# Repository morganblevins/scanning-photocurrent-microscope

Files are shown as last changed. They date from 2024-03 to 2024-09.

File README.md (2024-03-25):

# scanning-photocurrent-microscope

| Todos | Description + Statues |
| --- | --- |
| `Integrate visible laser into SPCM; get first reflection image` | **Done:** Results below |
| `Get visible light photocurrent scan from PbTaSe2` | **In progress** |
| `Integrate QCL into SPCM` | **Not started** Need to order periscope equiptment |

This repository contains the following for the scanning photocurrent microscope in MIT META lab:
* MATLAB code for controlling and collecting measurments
* Comprehensive part list and photo documentation of build
* Preliminary data

Example of a scanning reflection map of a 30 micron gold cross mark compared to a microscope image

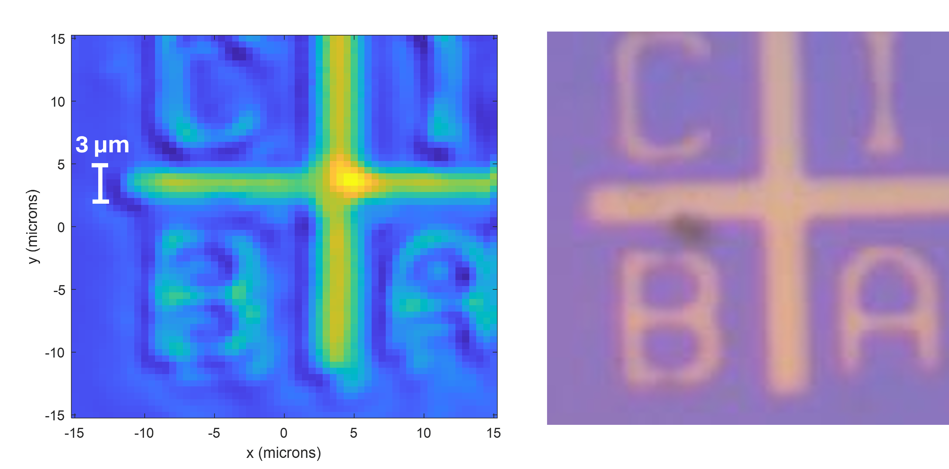
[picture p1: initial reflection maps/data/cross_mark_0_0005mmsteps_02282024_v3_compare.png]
Reflection map of 30 micron cross mark.


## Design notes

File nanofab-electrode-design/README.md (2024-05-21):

To use:
1. Run MatLab code and generate the input file to python code
2. Run Python code and generate the KLayout file.

On running MatLab code:
1. Change the electrodes length and width definitions for the electrodes, if needed. More notes below
2. Follow the prompts as they show up. Remember the order of corners when you click them (starts with 1) as you will be prompted to enter the two that will serve as the main electrode axis.

On running Python code:
1. Open KLayout Macro development, under "python", create a new "general macro (.lym)" file, paste the entire python code into the file;
2. Modify the input and output paths and file names given at the top of the code;
3. Modify route width, drawing layer, and the end electrodes width if needed;
4. Save and run the file in KLayout.

On opening the file in KLayout:
1. Open the silicon die template file in KLayout
2. While template file opened, go to "file -> open" again and open the file just generated by the code
3. Choose "add to current panel" when prompted

Things to note in MatLab code:
1. Electrodes width and length definitions are messed up. The value you enter will undergo transformations along with other shape objects and become some different value. May require some trial-and-error to find the right value.
2. Image does not display the order in which you clicked the corners, which can be hard to use since you have to remember it.

Things to note in Python code:
1. Routing modes are limited. Function docstrings in the code points to where they may be modified and improved
2. See details in routing main code docstring. Routing makes assumptions about which coordinates corresponds to nanostructure and electrodes, but these assumptions can actually be removed by interpreting the input file (from MatLab) differently, since the file indicates which coordinates are nanostructure and which are electrodes (right now these text indications are being ignored)



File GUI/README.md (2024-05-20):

GUI for the SPCM coded in MATLAB by Brady Cruse during Spring 2024 UROP

The GUI is broke up into 5 files

-BBD302_control_keithely2400

-Connection.m

-disconnected.m

-Home.m

The main app is coded in 'GUI.mlapp'.

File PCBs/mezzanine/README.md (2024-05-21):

Mezzanine PCB designed by Jacqueline Wang during Spring 2024 UROP using KiCAD

https://gitlab.com/kicad/libraries/kicad-footprint-generator

the silicondie.py file was ran inside the library-> KiCADModTree->examples folder
### Rendering


### Pad numbering


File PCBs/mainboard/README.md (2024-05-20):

Mainboad PCB files created by Brady Cruse during Spring 2024 UROP using Altium and EasyEDA

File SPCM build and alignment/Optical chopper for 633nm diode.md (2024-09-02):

**August 29th, 2024**

Note, <span style="color: black;">I followed the alignment procedure in the “alignment procedure” document. <span style="color: black;">Very important to have alignment of the beamsplitter, compensator, and the objective and PMT.</span></span>

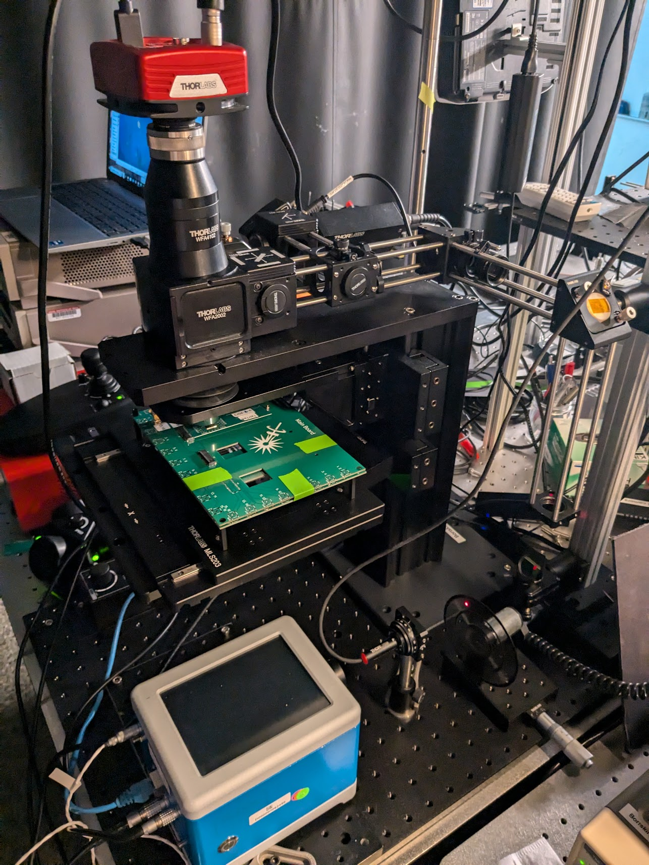
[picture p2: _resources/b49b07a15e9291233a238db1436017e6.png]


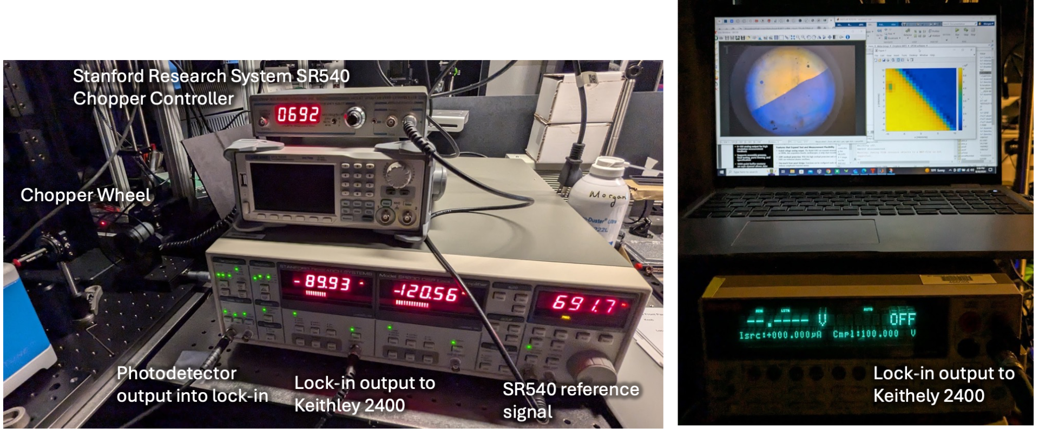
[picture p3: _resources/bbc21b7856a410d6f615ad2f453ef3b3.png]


**Procedure:**

1.  1<span style="color: black;">Position the chopper wheel in front of the laser such that the laser hits the outer slots</span>
2.  <span style="color: black;">Connect the SR540 ‘f’ output to the the reference input of the SR830 Lock-in amp</span>
3.  <span style="color: black;">Turn on the SR540 and set to desired frequency (avoid 60 Hz and its harmonics)</span>
4.  <span style="color: black;">The SR830 lock in should immediately pick up the reference frequency and track is very easily</span>
5.  <span style="color: black;">Connect the photodetector output to the SR830 input A and select current measurement</span>
6.  <span style="color: black;">Set SR830 Channel 1 to display X or R (I did X in this test)</span>
7.  <span style="color: black;">Set SR830 Channel 2 to display phase (theta)</span>
8.  <span style="color: black;">Adjust setting of SR830 until Channel 2 phase is constant (follow 2f rule,</span> <span style="color: black;">etc</span><span style="color: black;">)</span>
9.  <span style="color: black;">Connect the Channel 1 output to the Keithley 2400 and perform a scanning map over a gold-silicon interface on a wafer</span>

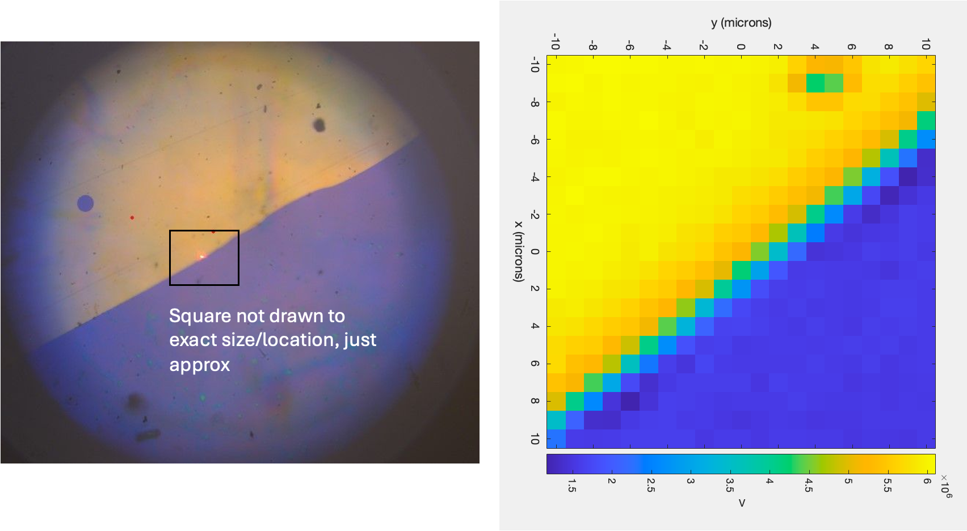
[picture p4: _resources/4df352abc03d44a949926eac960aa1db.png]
<span style="color: black;"></span>

<span style="color: black;"><span style="color: black;">This is the best reflection map I’ve ever gotten!! The gradation is</span> <span style="color: black;">really nice</span> <span style="color: black;">and exact. And it seems to even pick up a little hole in the upper right side.</span></span>

Note,

- <span style="color: black;">The PMT gets saturated depending on the gain you use to power it, so it may show “overload” if the conditions are too bright in the room. Reduce gain or lower lighting</span>
- There is an extra 635 bandpass filter in Mathias’ cupboard- may add this in front of the PMT to get rid of this issue.
- In this test I used a 30ND filter and had 1 small over-the-optical-bench light on

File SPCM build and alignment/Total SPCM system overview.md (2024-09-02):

# Overview of systems

The SPCM takes simultaneous photocurrent and reflection maps 

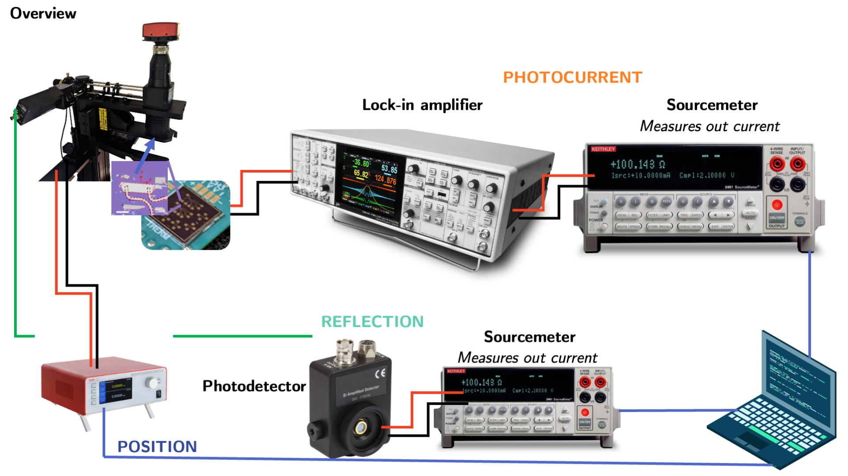
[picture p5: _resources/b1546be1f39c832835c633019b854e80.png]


# Optics

## <span style="color: black;">Optical path from lasers to samples</span>

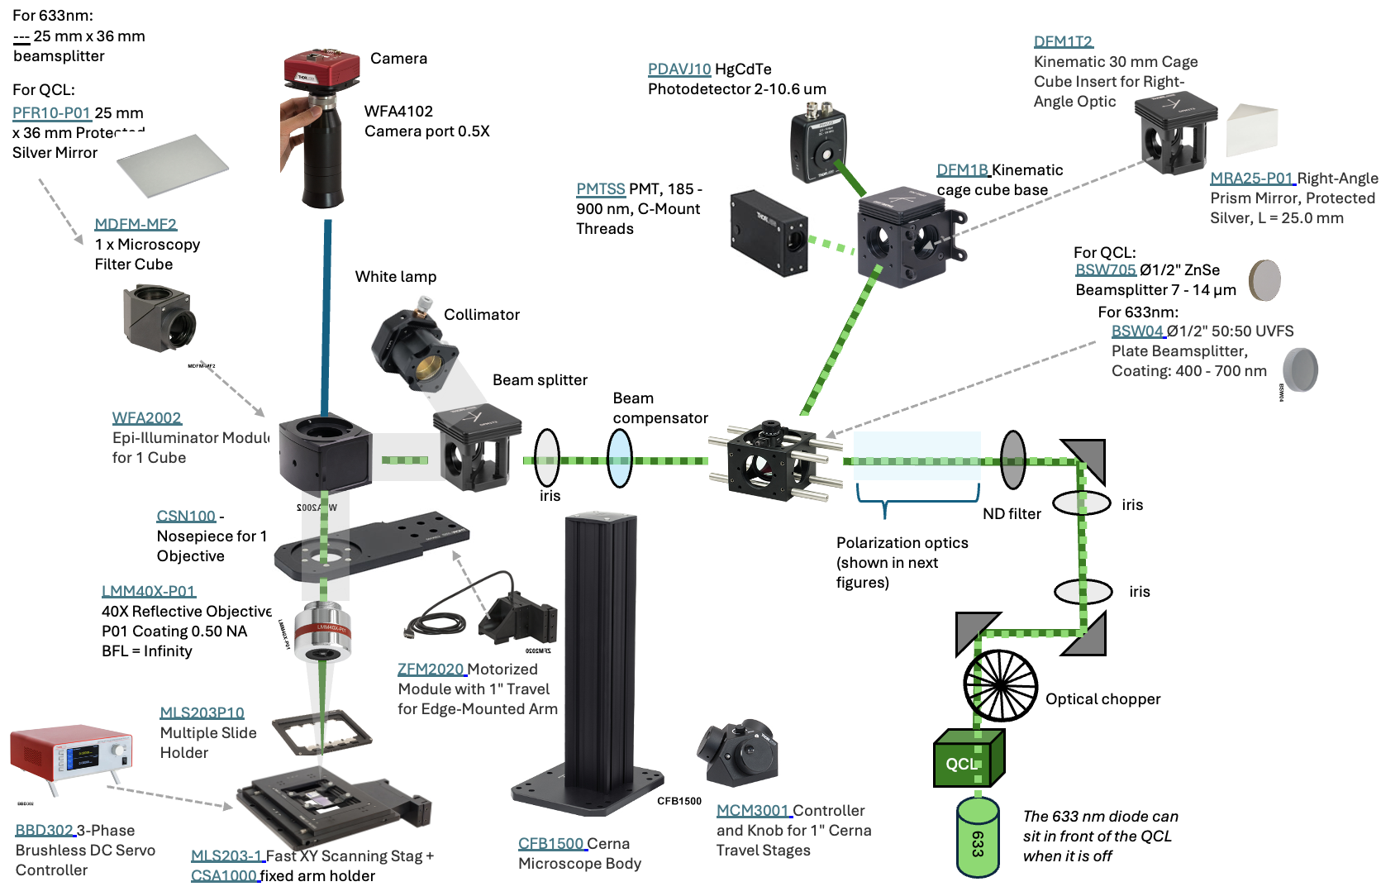
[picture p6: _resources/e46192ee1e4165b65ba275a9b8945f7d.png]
<span style="color: black;"></span>

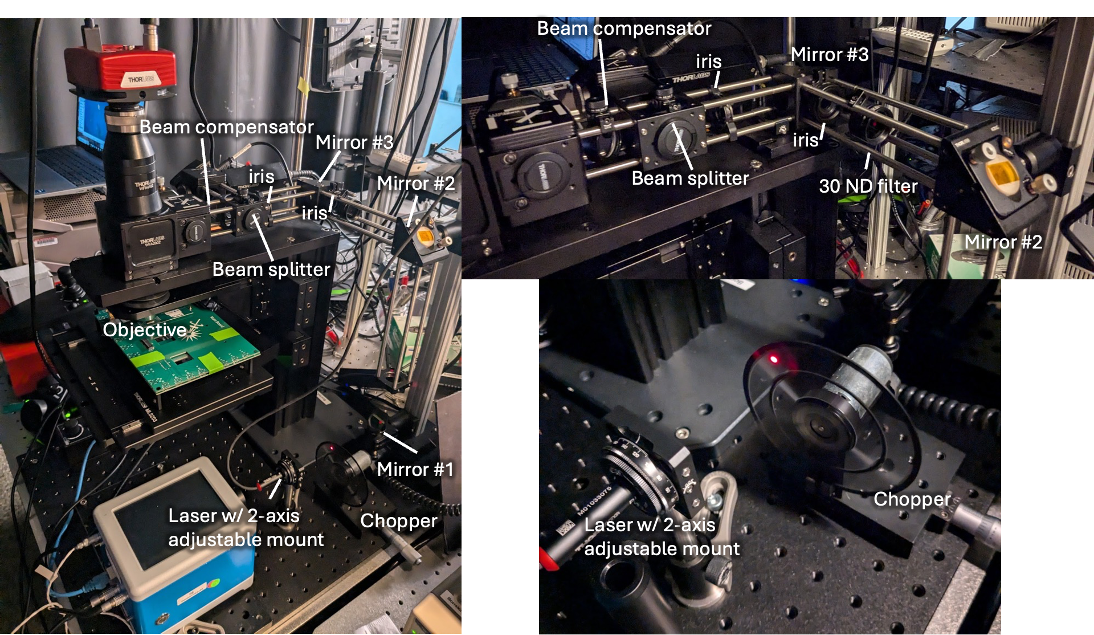
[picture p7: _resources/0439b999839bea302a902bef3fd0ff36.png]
<span style="color: black;"></span>

## <span style="color: black;"><span style="color: black;">Polarization optics for 633 nm laser diode</span></span>

### <span style="color: black;">C</span><span style="color: black;">reating linearly polarized 633 nm laser diode</span>

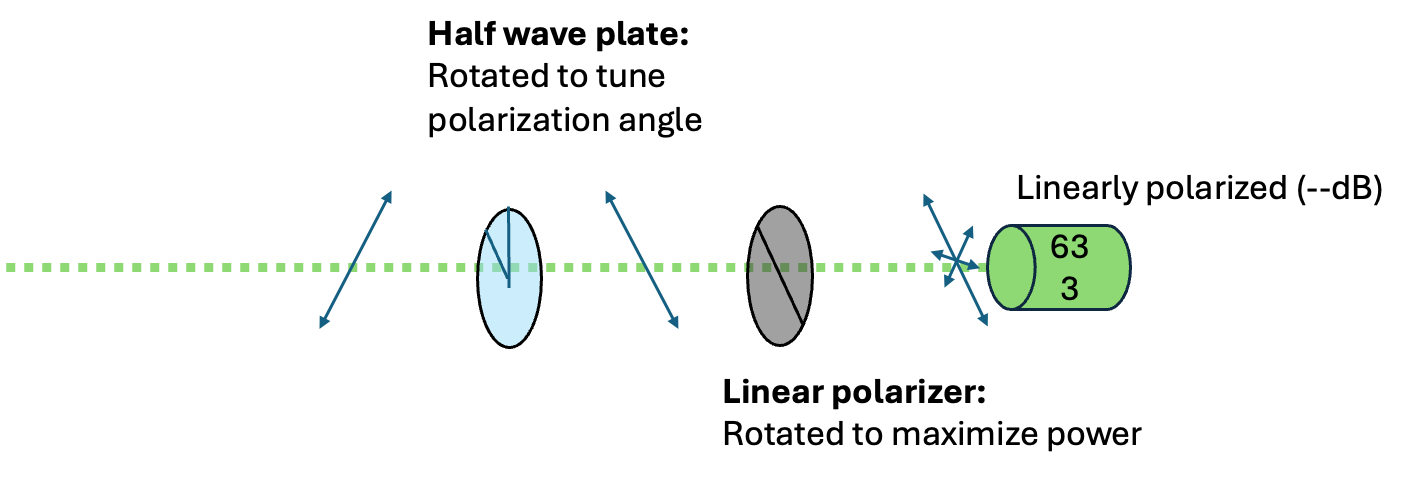
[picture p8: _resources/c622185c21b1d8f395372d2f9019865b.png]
<span style="color: black;"></span>

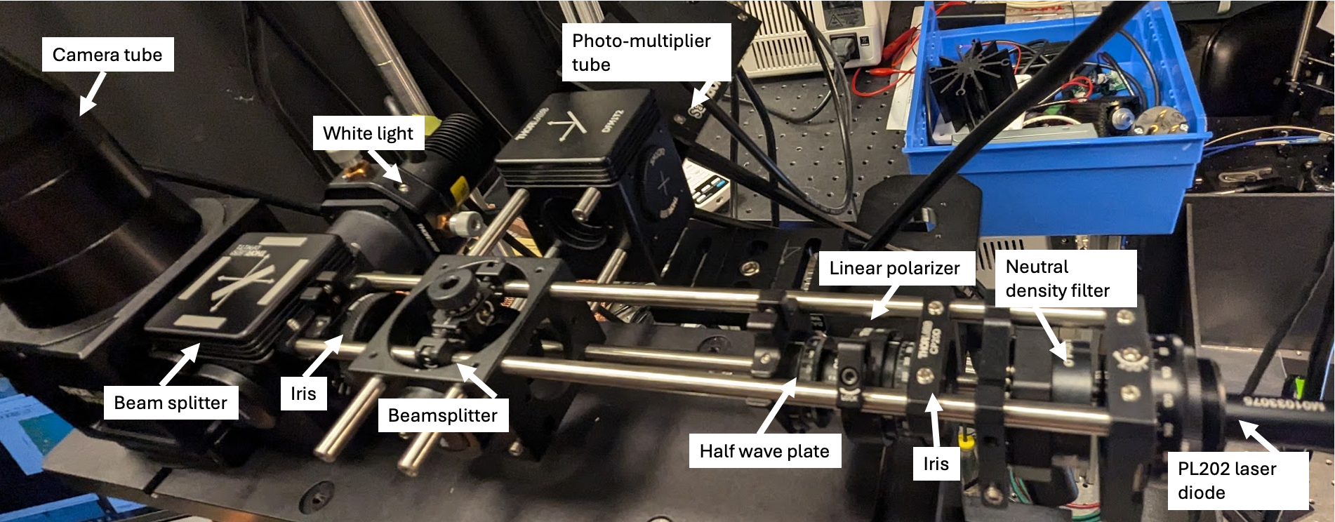
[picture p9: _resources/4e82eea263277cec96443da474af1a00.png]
<span style="color: black;"></span>

### <span style="color: black;"><span style="color: black;">C</span><span style="color: black;">reating circularly polarized 633 nm laser diode</span></span>

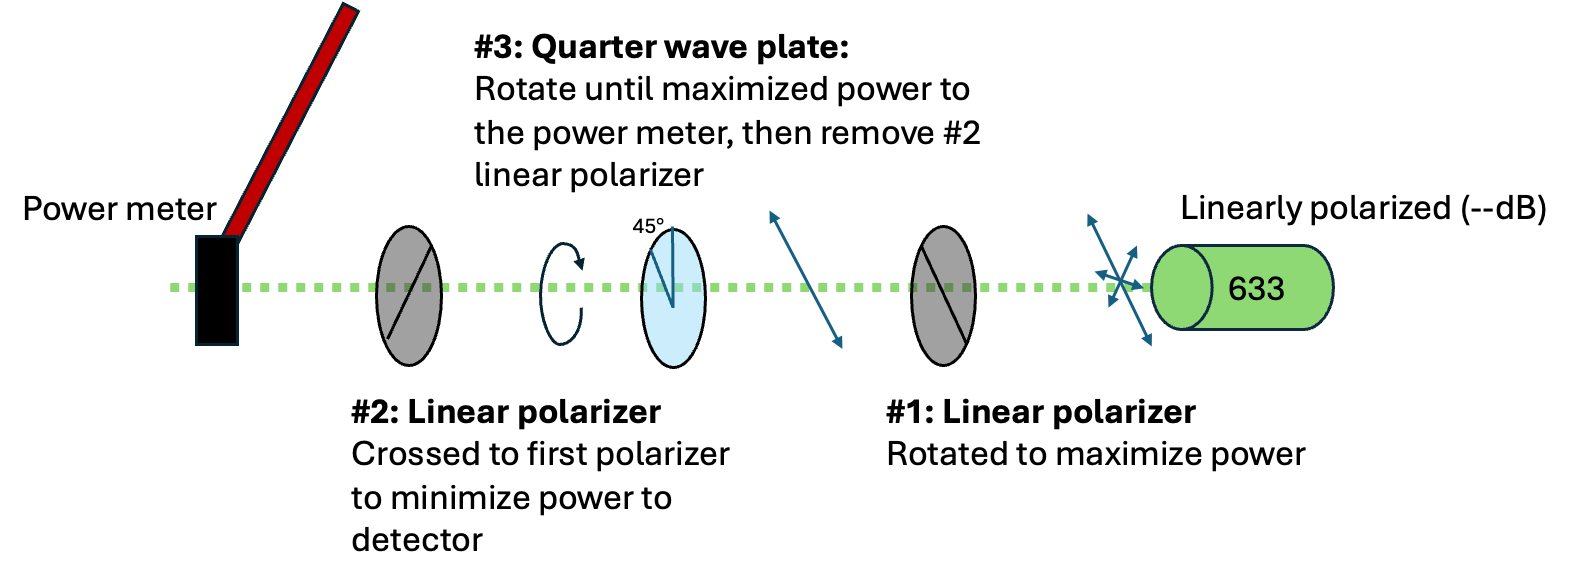
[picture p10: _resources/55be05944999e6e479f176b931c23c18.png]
<span style="color: black;"><span style="color: black;"></span></span>

<span style="color: black;"><span style="color: black;"><span style="color: black;">Two linear polarizers are used before and after the QWP along with a power meter. I kept the first LP static, so it still maximizes the power out of the PL202 laser. Then, without the QWP in the system, I crossed the two polarizers so that no power reached the power meter. Then I added the QWP between them and rotated it until I maximized power to the power meter. This occurs when the fast axis of the QWP is 45 degrees rotated from the input linearly polarized light. Thus, when I remove the second LP, I have circularly polarized light (illustrated in the Edmund optics diagram below).</span></span></span>

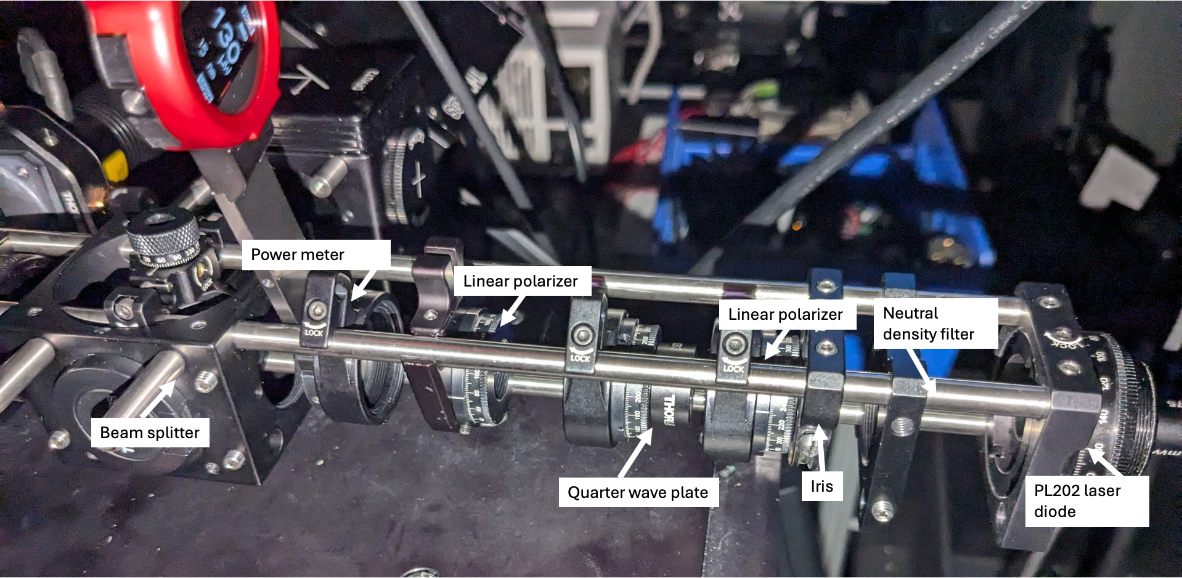
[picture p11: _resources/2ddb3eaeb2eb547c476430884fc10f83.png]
<span style="color: black;"><span style="color: black;"><span style="color: black;"></span></span></span>

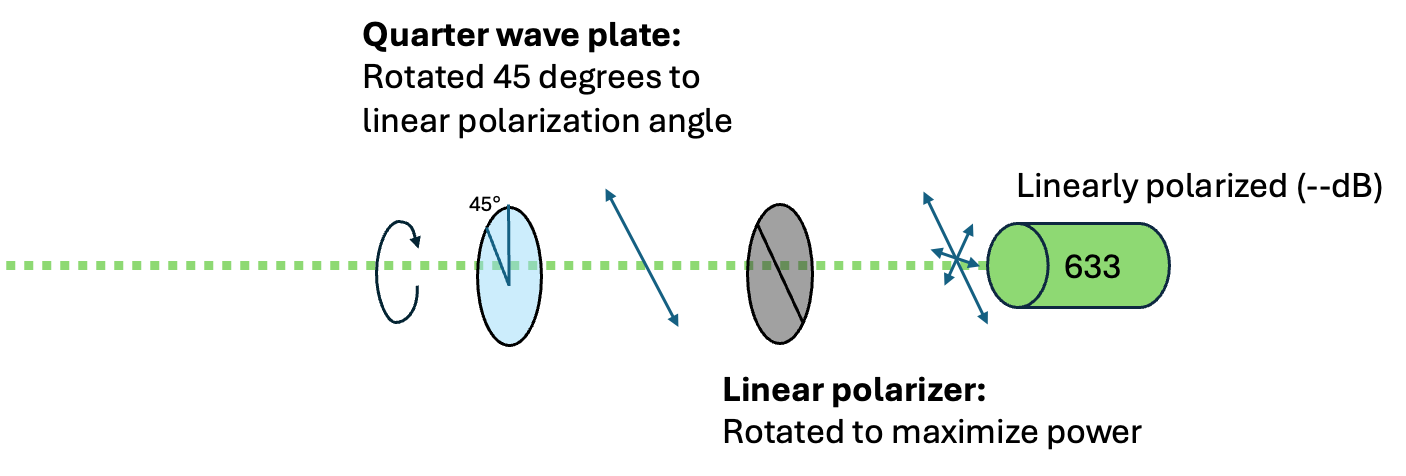
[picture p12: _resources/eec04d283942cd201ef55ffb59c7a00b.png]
<span style="color: black;"><span style="color: black;"><span style="color: black;"></span></span></span>

# <span style="color: black;">Electronics</span>

## <span style="color: black;"><span style="color: black;">PCB for interfacing silicon die samples</span></span>

<span style="color: black;"><span style="color: black;">Designed by Brady and Jacqueline</span></span>

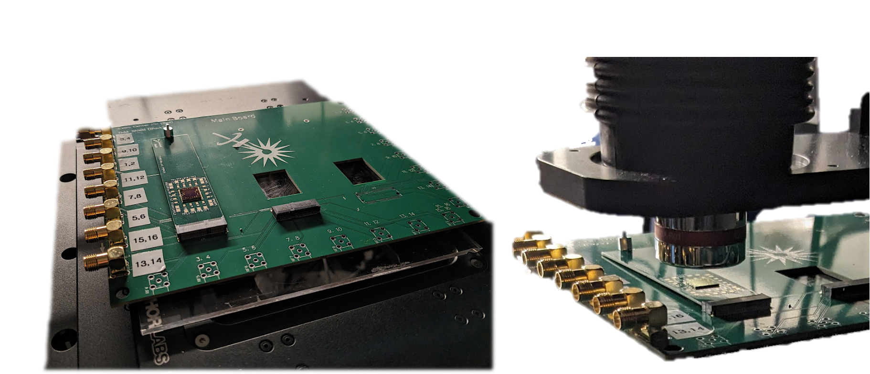
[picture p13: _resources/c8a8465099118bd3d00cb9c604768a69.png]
<span style="color: black;"><span style="color: black;"></span></span>

## <span style="color: black;"><span style="color: black;"><span style="color: #767676;"><span style="color: black;">Measuring</span> <span style="color: black;">current from photodetectors/</span><span style="color: black;">PCBs</span></span></span></span>



See "Optical chopper for 633 nm..." document for procedure

## Triggering QCL

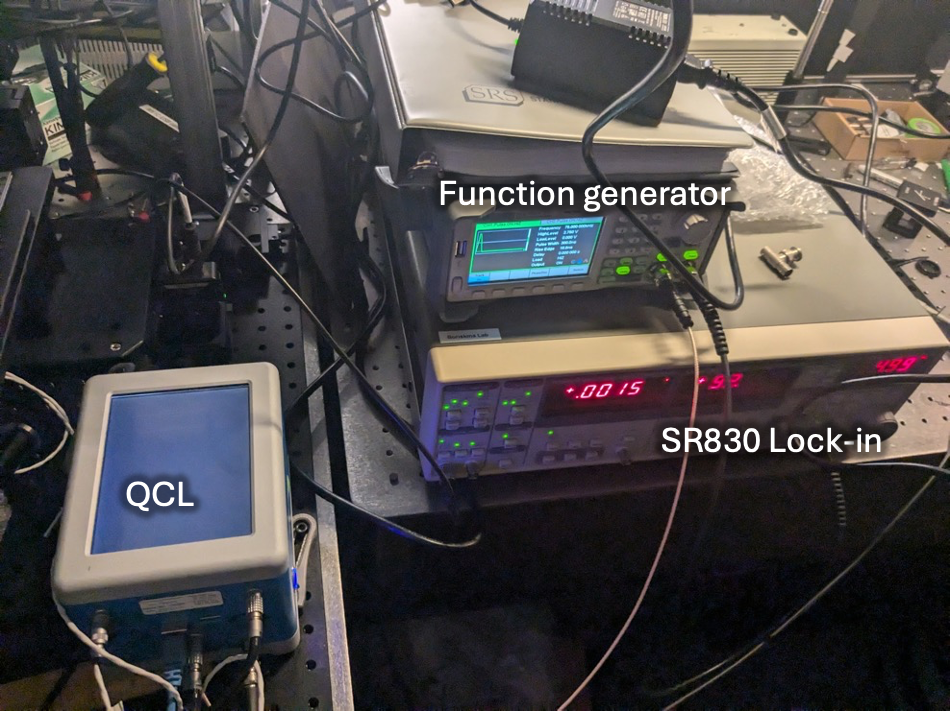
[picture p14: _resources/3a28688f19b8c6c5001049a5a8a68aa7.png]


<span style="color: black;">Follow procedure in “QCL with</span> <span style="color: black;">func</span> <span style="color: black;">gen and lock in</span> <span style="color: black;">amplifier.pptx</span><span style="color: black;">”</span>

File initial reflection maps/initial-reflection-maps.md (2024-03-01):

Reflection map of 30 micron gold cross mark

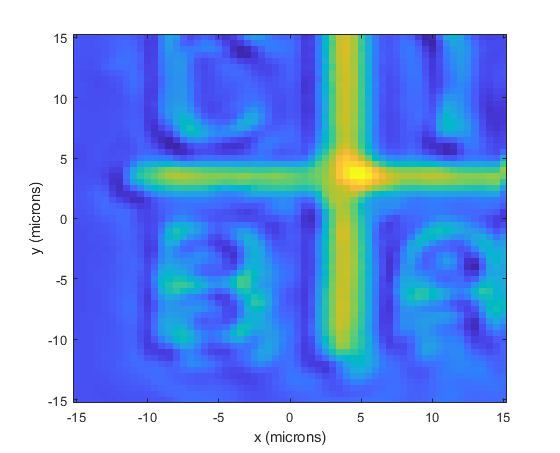
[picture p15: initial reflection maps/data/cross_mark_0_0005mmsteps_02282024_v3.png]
Reflection map of 30 micron cross mark.


Reflection map of 30 micron gold cross mark compared to microscope image

Reflection map of 30 micron cross mark.

Microscope images:

Laser off             |Laser on
:-------------------------:|:-------------------------:
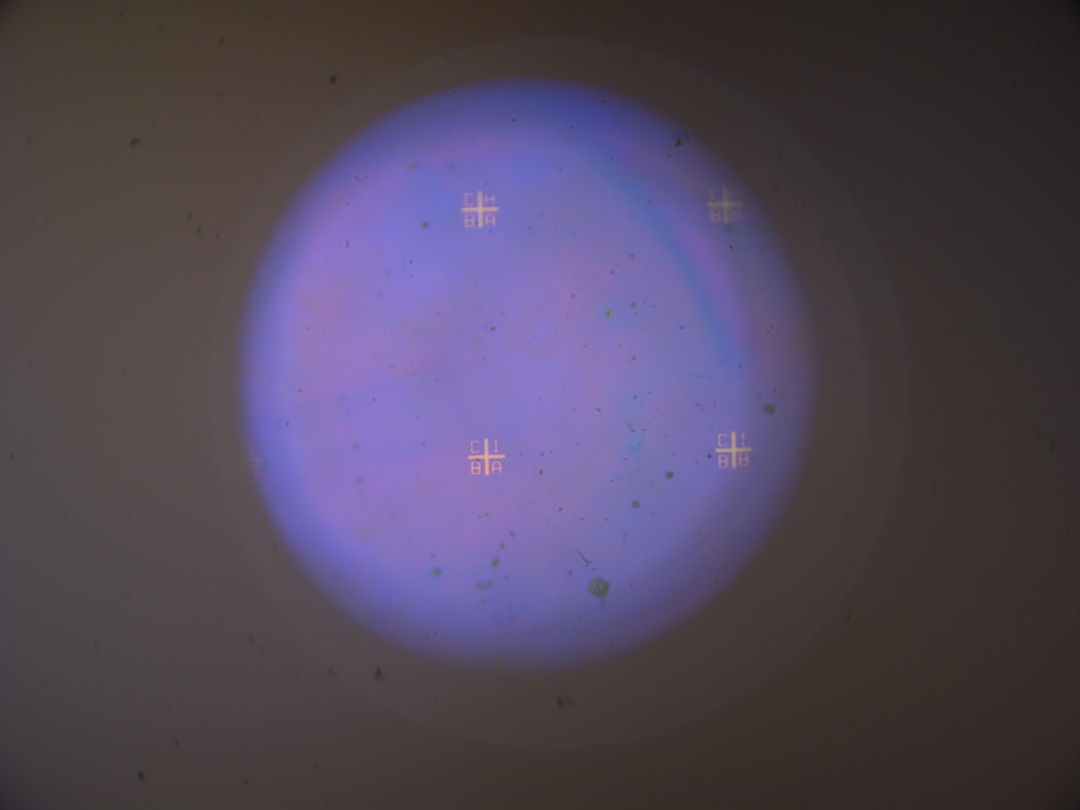
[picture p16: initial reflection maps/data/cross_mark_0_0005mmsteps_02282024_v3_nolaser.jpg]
Microscope image of 30 micron gold cross mark
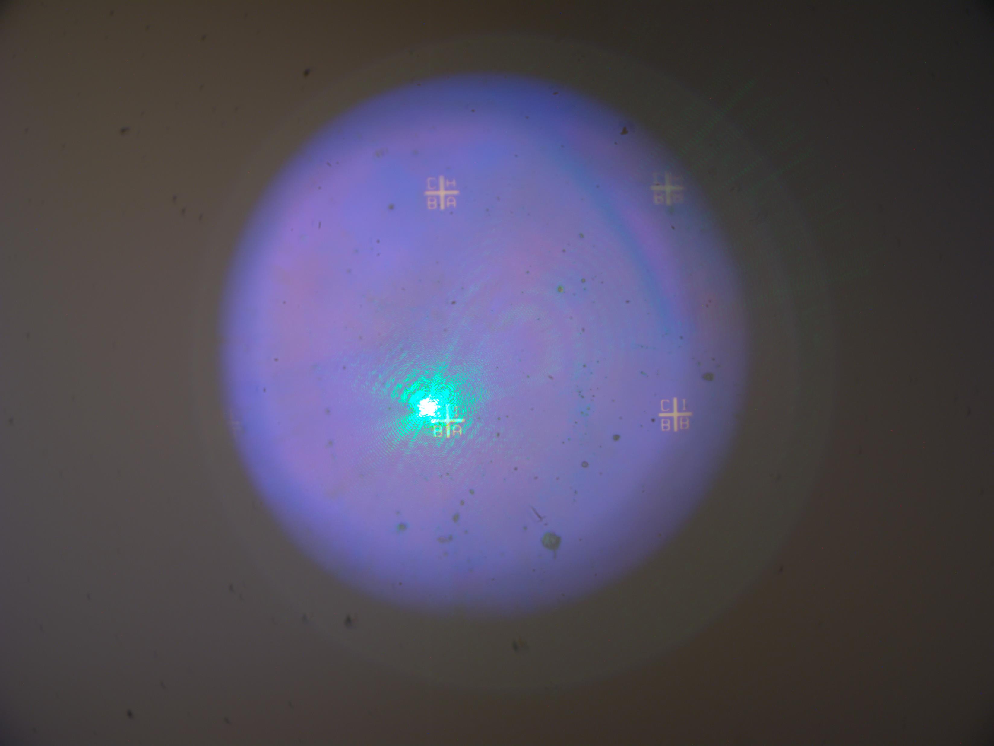
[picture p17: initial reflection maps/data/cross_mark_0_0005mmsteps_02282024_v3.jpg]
Microscope image of 30 micron gold cross mark wiht laser spot
  |

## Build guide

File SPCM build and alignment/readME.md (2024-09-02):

Information on the status of scanning photocurrent microscope (SPCM) system in the Boriskina lab and its alignment procedure

To start, here is an [overview of the entire SPCM system](Total%20SPCM%20system%20overview.md).

[Here](PCBs%20and%20samples.md) is what the samples for the SPCM look like and how they attach to PCBs and the electronics of the system.

And, getting more into the weeds, here is [how to optically align the system](Alignment%20procedure%20for%20SPCM.md), how to integrate the [quantum cascade laser](QCL%20integration.md) and how to add in an [optical chopper system ](Optical%20chopper%20for%20633nm%20diode.md)

And here is a reminder of the goal of a SPCM:

The Scanning Photocurrent Microscope (SPCM) setup measures simultaneous maps of the photocurrent and reflection of a target material. These maps reveal the underlying physics of photocurrents in materials by revealing the spatial location of currents and their direction. 
SPCM studies are key to understanding the origins of the photogalvanic effect (PGE), an effect which enables spontaneous, p-n junction-less photocurrents in inversion symmetry-breaking materials. The linear PGE (LPGE), also called shift current, is manifested as the shift in space of a charge carrier during the inter-band photoexcitation process under illumination by linearly polarized light, stemming from the I-symmetry breaking of the material (Dai 2023).  Berry flux fields contribute to shift current, making WSMs attractive material candidates for observing this effect (Liu 2020, Weng 2019, Osterhoudt). In the circular PGE (CPGE), illumination from circularly polarized light selectively excites charge carriers with preferred linear momenta supporting a net photocurrent in certain symmetry groups of I-symmetry-breaking WSM or strained DSM materials.
Additionally, the PGE can be unlocked in centrosymmetric materials by engineering strain gradients into the materials, a technique called “flexoelectricity”. SPCM measurements of photocurrents in these samples are especially important for understanding this effect and identifying flexoelectric coefficient in candidate materials.
 
From Lai et al 2022: (d) Scanning reflection image and (e,f) photocurrent microscopy images of a TaIrTe4 device with U-shaped electrodes at room temperature with 633 nm (e) and 4 µm (f) excitation. 



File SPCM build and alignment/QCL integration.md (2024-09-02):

**August 20th (ish), 2024**

- **QCL** is integrated into SPCM and being triggered by a function generator which is also triggering the lock-in ampliflier
- The optical path is quick to align using the red guiding laser and the 3 adjustable mirrors
- HOWEVER, alignment with the beamsplitter (enabling reflection mapping is currently not done. I believe we need to compensate for the translation of the beam (like we do for the 633nm laser diode) but this is now much harder when you can't see the beam!!

Setup:

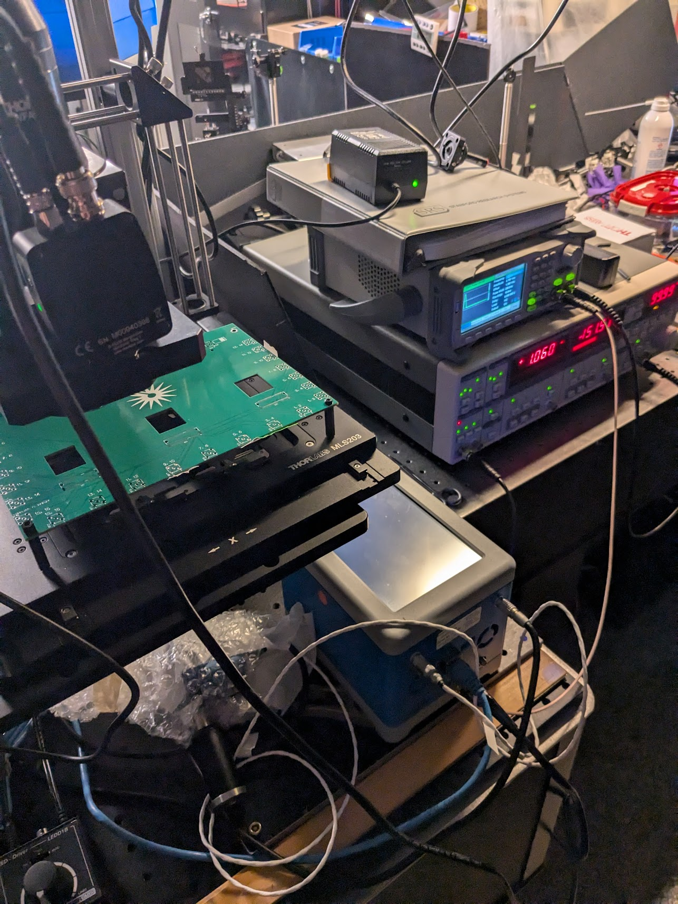
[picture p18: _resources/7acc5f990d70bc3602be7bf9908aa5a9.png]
Í

Confirming that the QCL is aligned using the MCT at the WFA2002, reading detector output with the lock-in:

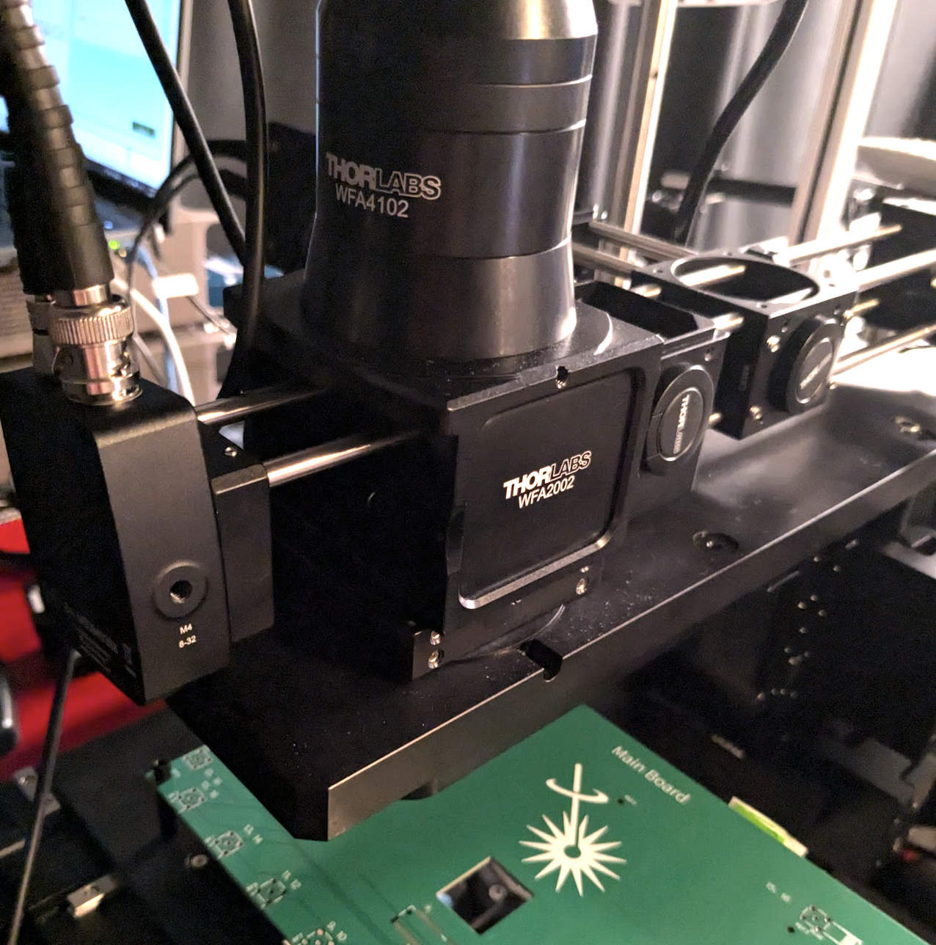
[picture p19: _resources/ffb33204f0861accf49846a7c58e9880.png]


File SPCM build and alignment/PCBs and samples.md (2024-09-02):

## Overview of SPCM and sample under study

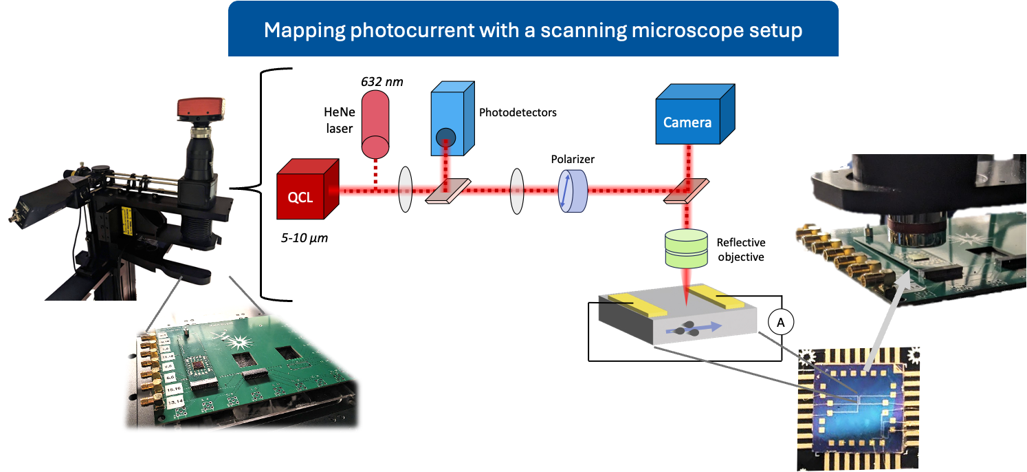
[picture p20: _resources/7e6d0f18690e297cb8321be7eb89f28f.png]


## The PCBs interface the silicon die samples to current meters

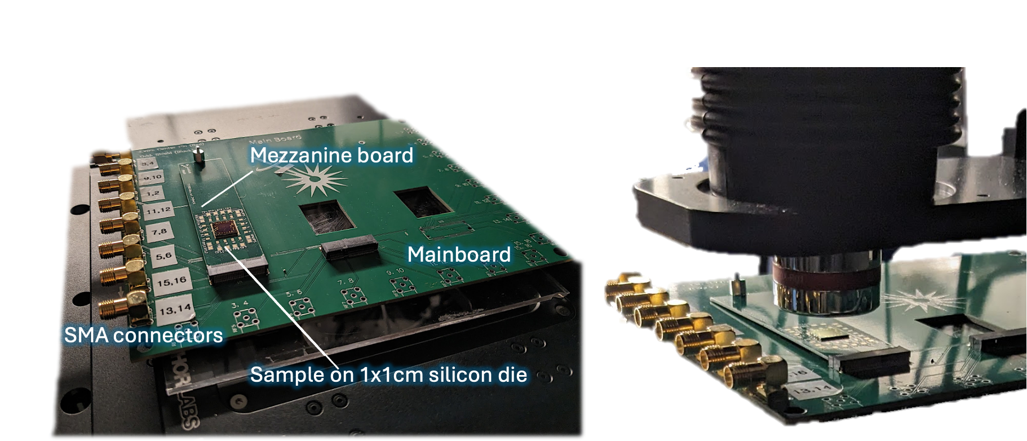
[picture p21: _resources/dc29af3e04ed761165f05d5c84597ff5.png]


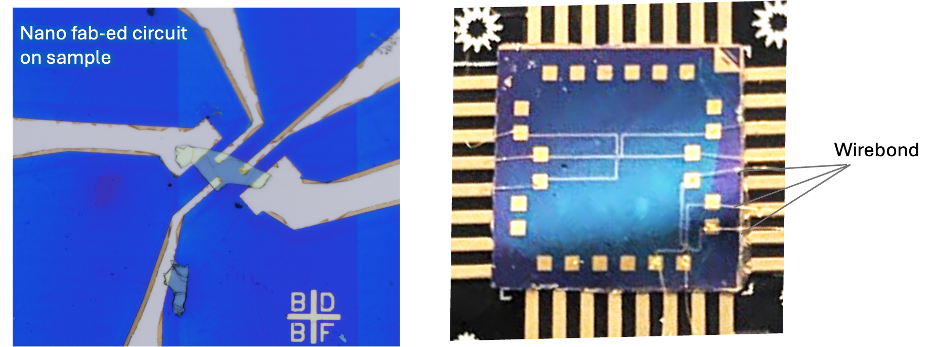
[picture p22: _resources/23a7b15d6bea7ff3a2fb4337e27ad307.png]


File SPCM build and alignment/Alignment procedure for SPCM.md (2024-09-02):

**August 30th, 2024**

This outlines the alignment procedure for the 633 nm laser diode in the Boriskina Lab SPCM as of August 2024. This procedure has so far given the best reflection mapping results.

**Current SPCM setup:**

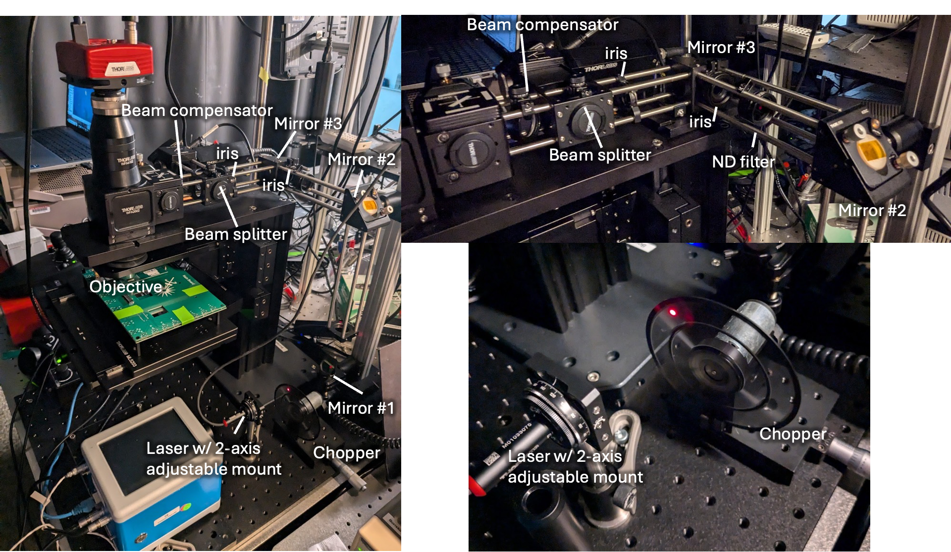
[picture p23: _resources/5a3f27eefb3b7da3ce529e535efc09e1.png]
****

**Step 1:** Adjust mirror #1 and #2 (or #1 and the laser holder) back and forth until the laser is aligned all along the cage section when the iris is moved back and forth

<span style="color: black;">Note: I had to be</span> <span style="color: black;">pretty careful</span> <span style="color: black;">about how I locked down</span> <span style="color: black;">the</span> <span style="color: black;">mirror</span> <span style="color: black;">#2</span> <span style="color: black;">to</span> <span style="color: black;">the</span> <span style="color: black;">vertical</span> <span style="color: black;">post. If its too high or</span> <span style="color: black;">low</span> <span style="color: black;">it bends the posts and make the system un-level.</span>

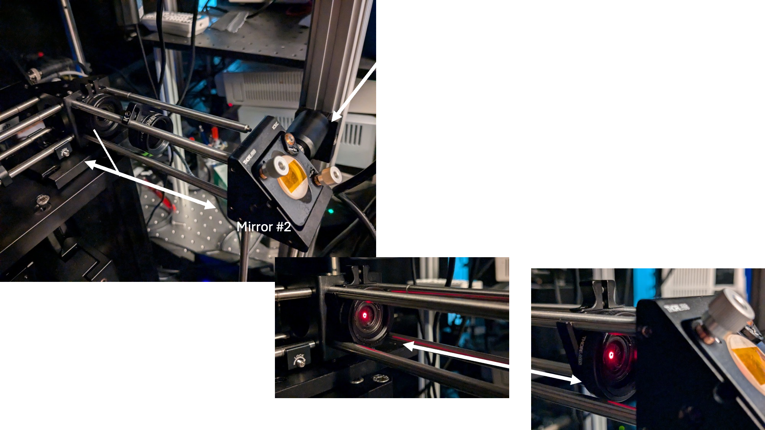
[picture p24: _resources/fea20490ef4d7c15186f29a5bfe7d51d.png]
****

**Step 2:** <span style="color: black;">Adjust mirror #3 until the laser is centered in the iris</span>

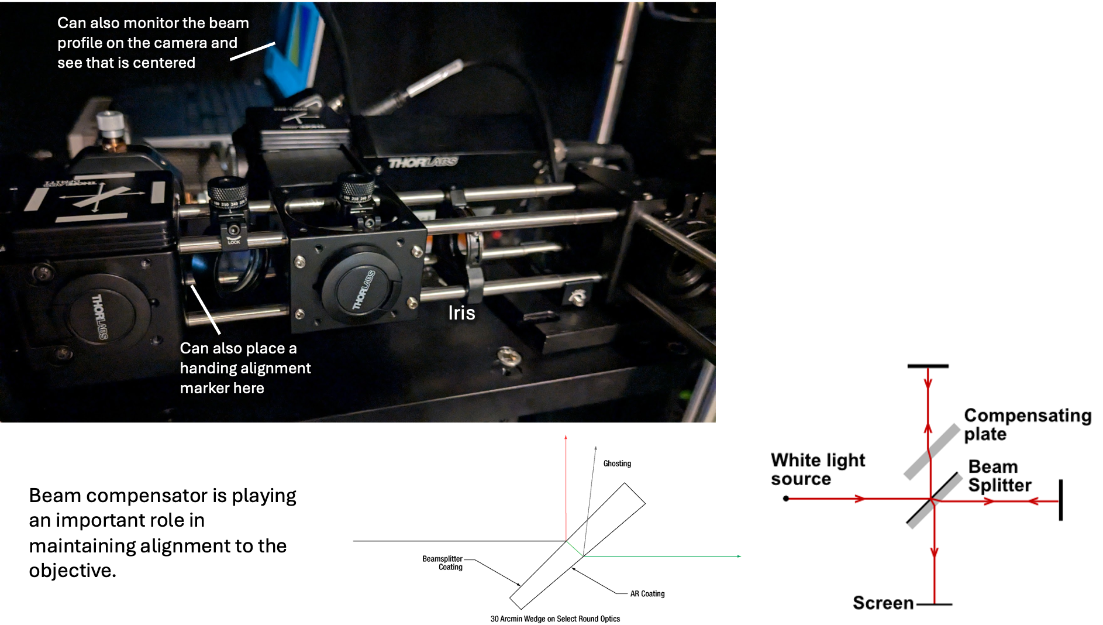
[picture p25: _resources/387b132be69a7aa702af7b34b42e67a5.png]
****

**NOTE:** Beam compensation must be properly aligned to the optical path and the beamsplitter

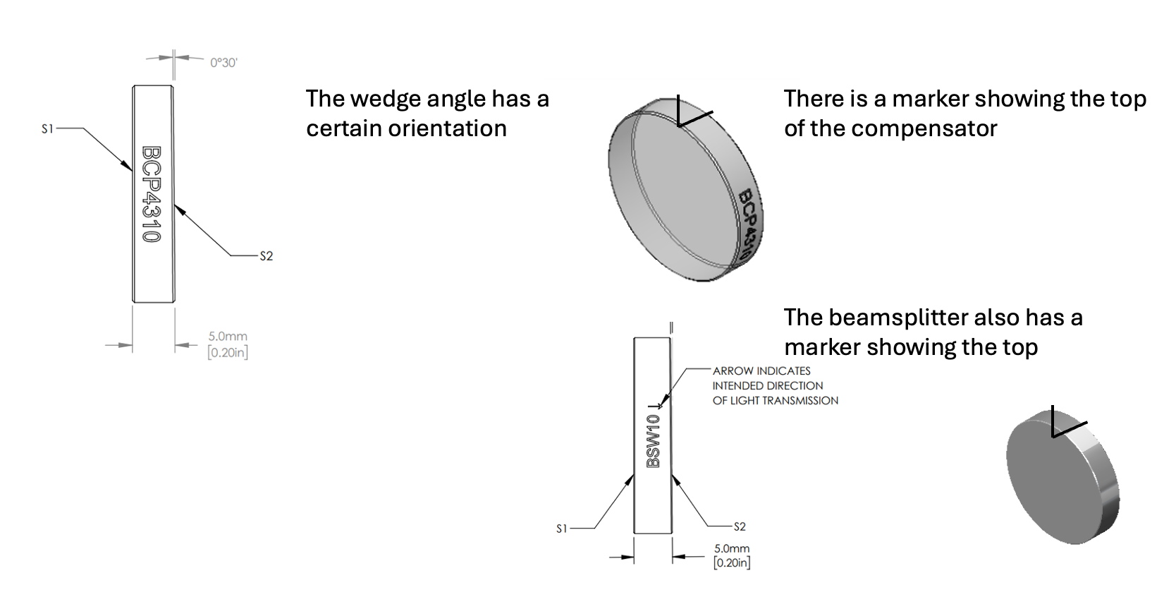
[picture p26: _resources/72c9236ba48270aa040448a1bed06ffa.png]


<span style="color: black;">Below shows how the addition of the beamsplitter translates the beam without a compensator:</span>

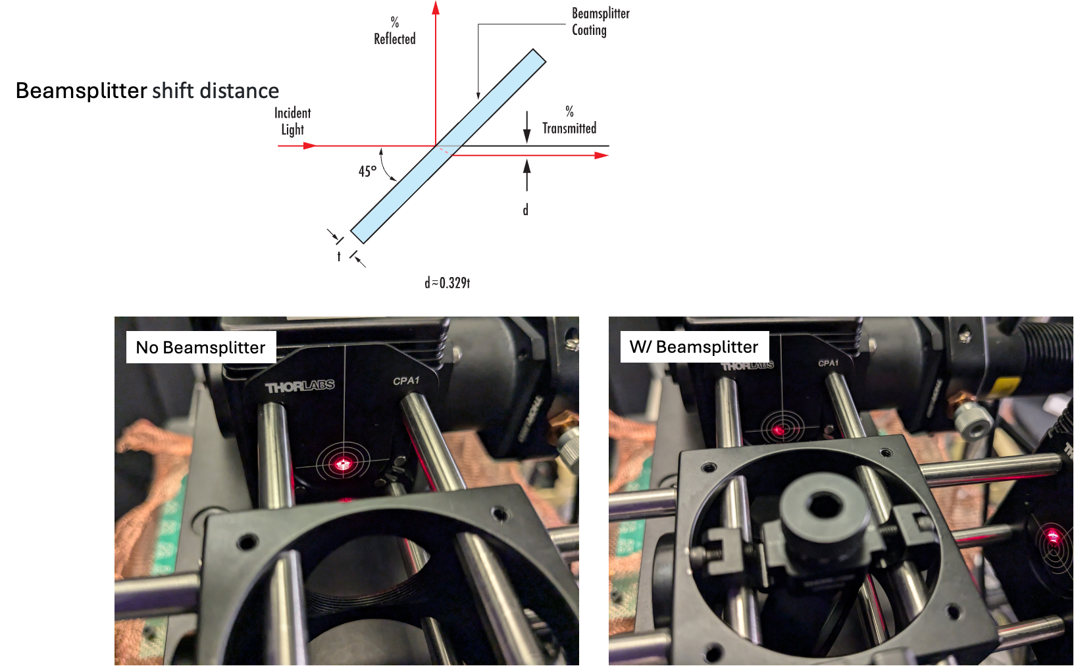
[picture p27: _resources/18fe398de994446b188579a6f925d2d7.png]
<span style="color: black;">****</span>

<span style="color: black;">**NOTE:** I’ve used a mounting base to tilt up the cage so it’s level.</span>

- <span style="color: black;">I used the level app on my phone</span>
- <span style="color: black;">In the future this should be done more exactly/precisely- should consult Thorlabs for best practice on this.</span>

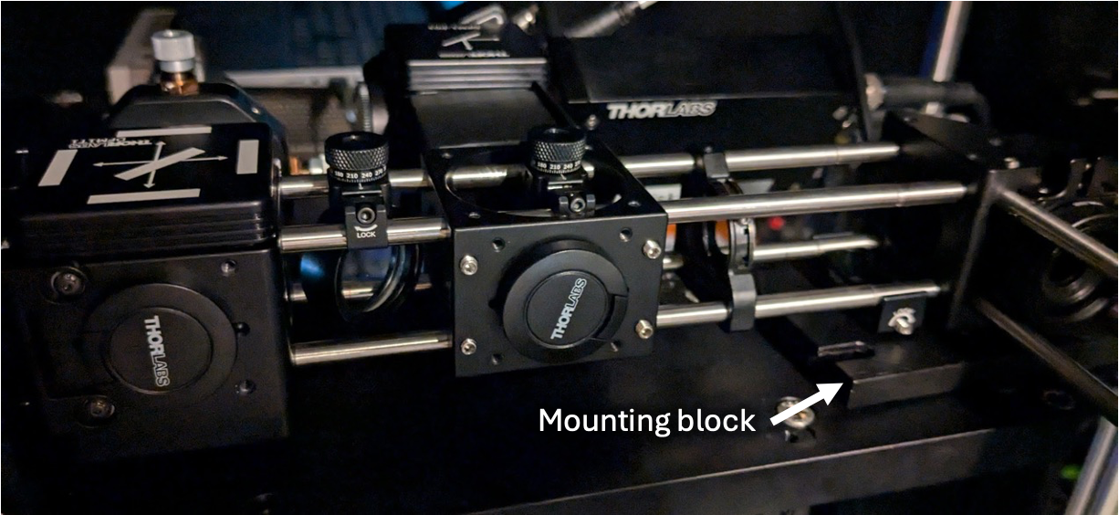
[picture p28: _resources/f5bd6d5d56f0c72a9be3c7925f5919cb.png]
<span style="color: black;"></span>

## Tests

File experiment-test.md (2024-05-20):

# SPCM Laboratory Notebook

Optical path:

```mermaid
graph LR
A[633 nm laser] -->B(ND filter)
    B --> C(1/2 W.P.)
    C --> D{B.S.}
    D --> E[PMT]
    D --> F{B.S.}
    G[Lamp] --> F
    F --> H{B.S.}
    H --> I(Camera)
    H --> J(Obj.)
    J --> K[Sample]
```

Optical path parts:

| Item              | Part # | About |
| :---------------- | :------: | ----: |
| 633 nm laser      |   P..   | diode |
| ND filter, 0.01\%        |   NE40A   | Neutral density filter |
| 1/2 Waveplate    |   ---   | Linear polarizer |
| Beamsplitter 1    |  False   | splits optical path to PMT |
| PMT |  False   | Photomultipler tube, measures refl. |
| Beamsplitter 2  |   P..   | diode |
| Beamsplitter 3  |   NE40A   | Neutral density filter |
| Camera tube    |  False   | splits optical path to PMT |
| Camera    |  False   | splits optical path to PMT |
| Objective |  False   | Photomultipler tube, measures refl. |

Starting with the "orange" flake on the PbTaSe2 chip 4. First I do a quick reflection map of a flake that is not part of the circuit to confirm the system is working.

flake_refl_test_camera

flake_refl_test

Next I perform a reflection map of the entire flake now that I see the setup is working. 

## Experiment Identifiers

Experiments conducted for the **Scanning Photocurrent Microscope** (SPCM) are identified as follows:

_KBSX-Y_

where
- KBS is the initials of the experimentalist (Klementine Burrell-Sander)
- X is a number used to identify the molecule
- Y is a number that indicates how many times the reaction has been repeated

For example, **KBS19-3** indicates the **third** attempt at synthesising molecule **KBS19**

Experiments conducted for The Breaking Good Project are identified as follows:

Year of program
Underscore
Program the molecule is contributing to e.g. SSP (The University of Sydney's Special Studies program), BG (breaking good core program)
Underscore
One number followed by a letter - the main identifier of the molecule that is being synthesised
Underscore
A number which indicates the batch number/number of attempts

For example, **2022_BG_1J_002** describes the **second** attempt at the synthesis of molecule **1J** for the core Breaking Good program ran in **2022**.

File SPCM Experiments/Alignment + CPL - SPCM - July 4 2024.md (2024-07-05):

## **Summary:**

The SPCM is at a state where all the optics and electronics are working in the set up. I believe that now if we have a sample with an expected photo response, we should be able to measure it. I've been testing on a PbTaSe2 sample and do not see any photo response for either linear or circularly polarized 635nm light. I think this is to be expected.

I currently have one TaIRTe4 and two Bi2Te3 samples. These need to be wire bonded but I should be able to measure them when I return from the GRC (I'll be back July 12). Wirebonding was rough when I tried last week so I hope it can be easier next time.i. These I expect to see photo response in that I should be able to measure. Also, I'll be adding the QCL to the light path when I return.

In terms of next steps, we currently have no more PPMS chips. Further, it would be nice to have more TaIrTe4 chips and any other materials that we can start measuring that we believe should have a response. And further, we should get strained samples with electrodes fabricated as well.

I am hoping Abhishek can help fabricate a new wafer of PPMS chips. Depending on the timeline of that we could try to get several more samples prepared in July in coordination with Zach's transfer setup.

## **Current optical path**



## **Quick reflection map test**

The alingment was improved yesterday - I want to see if I can get a quality reflection map using the ND40A (aka 0.01% transmission). I will use the PbTaSe2 chip that broke as my test device.

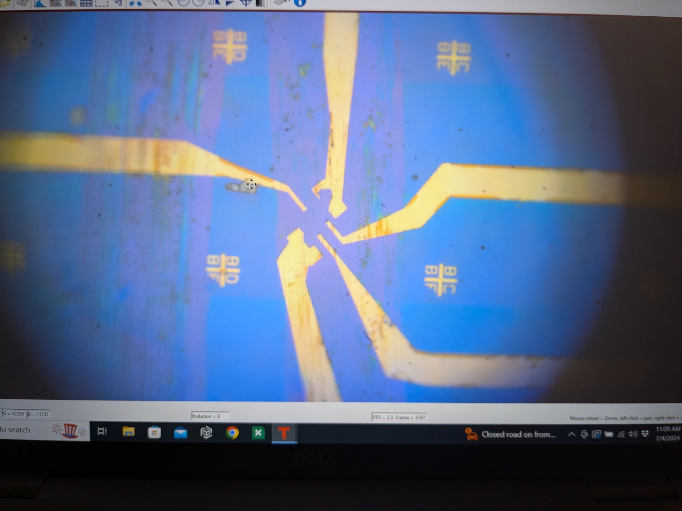
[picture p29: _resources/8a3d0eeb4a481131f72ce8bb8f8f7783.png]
&nbsp;

## Circularly Polarized Light with a QWL

I followed the protocol explain [this Thorlabs video.](https://www.youtube.com/watch?v=P0asuzX4x-Q)



Two linear polarizers are used before and after the QWP along with a power meter. I kept the first LP static, so it still maximizes the power out of the PL202 laser. Then, without the QWP in the system, I crossed the two polarizers so that no power reached the power meter. Then I added the QWP between them and rotated it until I maximized power to the power meter. This occurs when the fast axis of the QWP is 45 degrees rotated from the input linearly polarized light. Thus, when I remove the second LP, I have circularly polarized light (illustrated in the Edmund optics diagram below).

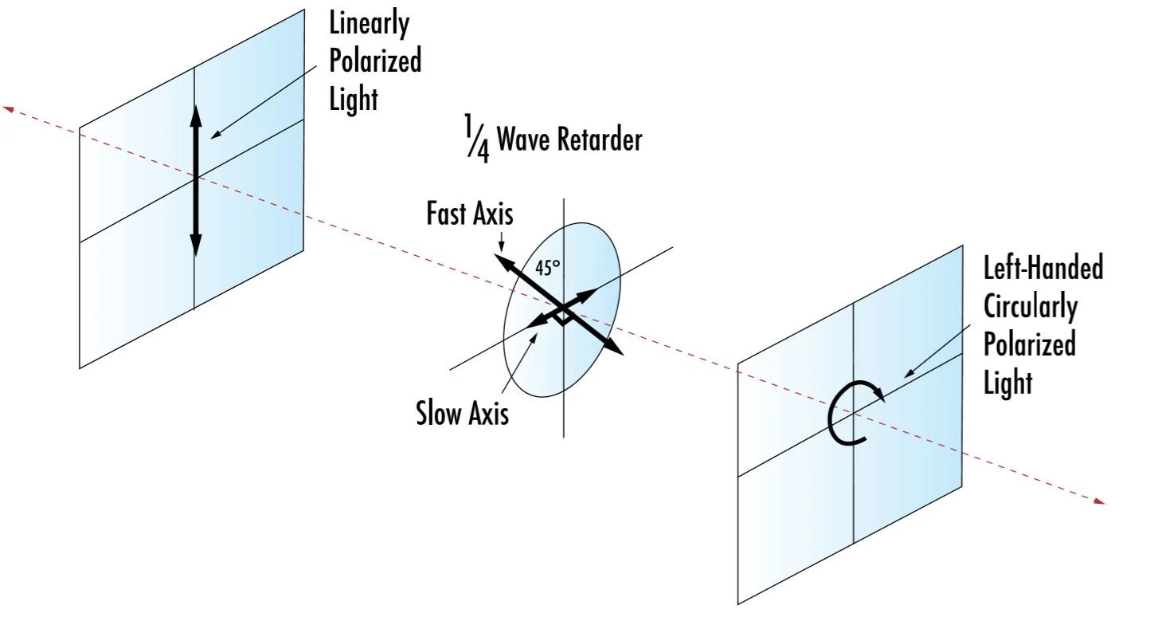
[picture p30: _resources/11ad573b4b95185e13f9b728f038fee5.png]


## Simultaneous photocurrent and reflection mapping

I use both channels of the Keithley 6482 picometer to perform simultaneous photocurrent and reflection mapping.

In the below image, channel 1 on the left shows no photocurrent and channel 2 on the right show the reflection from the electrodes on the PbTaSe2 sample as measured with the PMT. This is "PbTaSe2_5_30OD_CPL_2024-07-04-1436" aka sample "PbTaSe2_5" with a 30OD ND filter and with circularly polarized light.

While I kind of do not trust the wire bonds on the PbTaSe2 sample (resistance was reading >10 kOhms w/ the multimeter when I would expect hundreds) I do think that we are see evidence that the shielding around the SMA cable is working-- there is no interference pattern on the picometer measurement from the SMA sample.

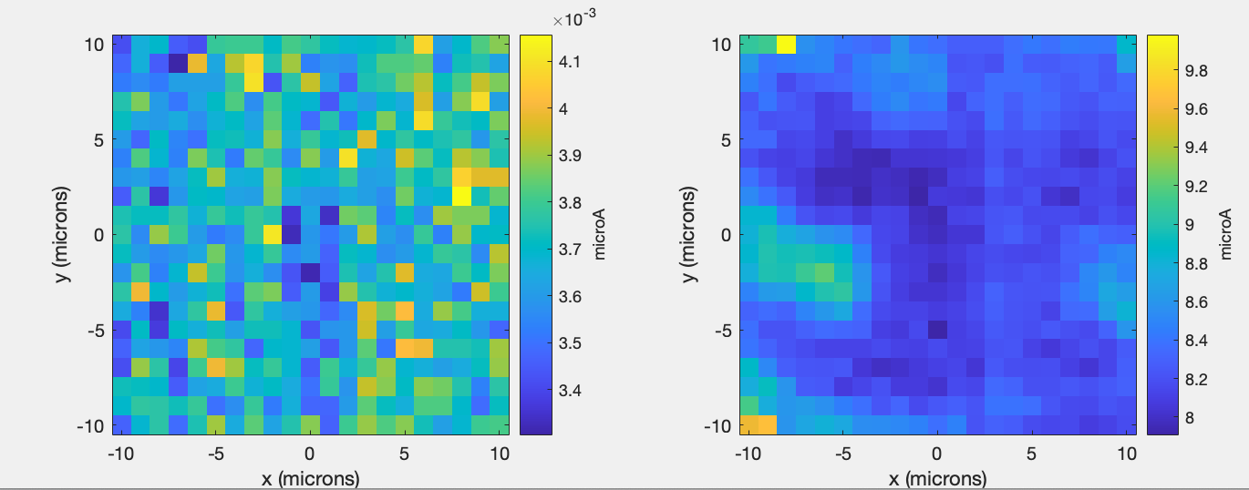
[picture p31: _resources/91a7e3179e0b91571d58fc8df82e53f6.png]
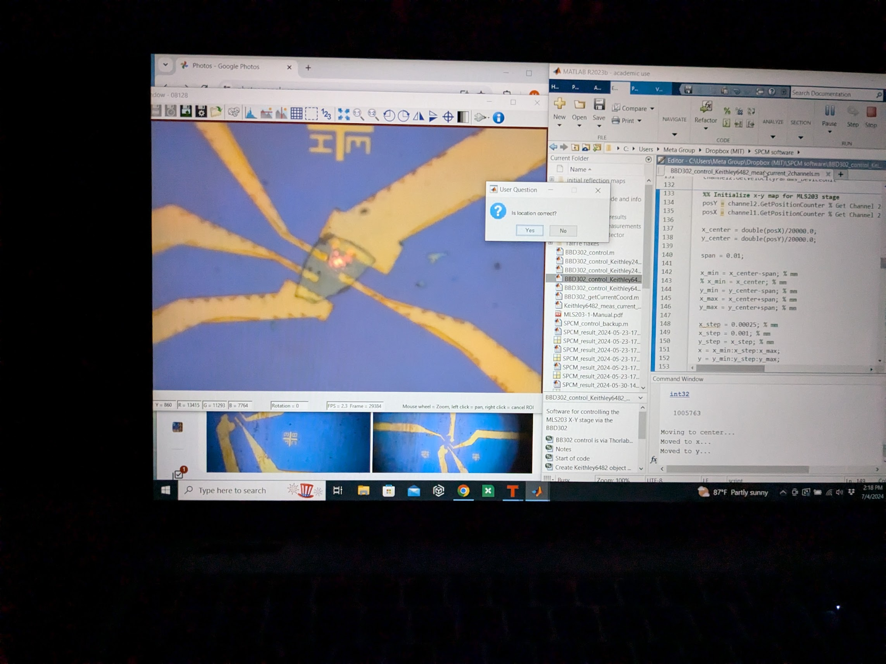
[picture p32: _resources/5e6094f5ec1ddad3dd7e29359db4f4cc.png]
 

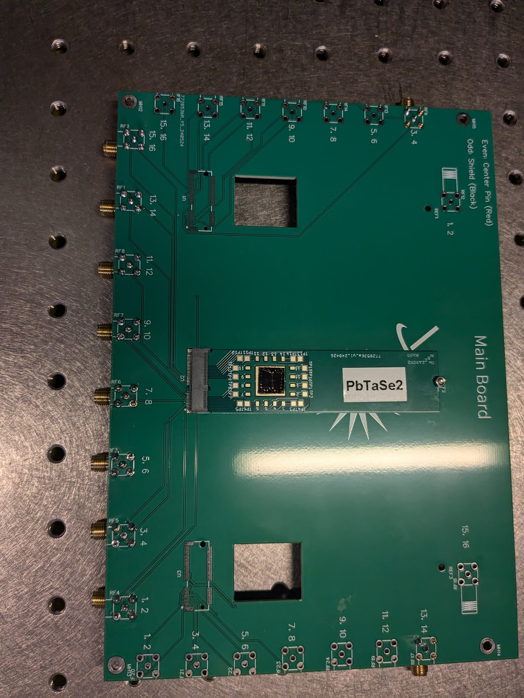
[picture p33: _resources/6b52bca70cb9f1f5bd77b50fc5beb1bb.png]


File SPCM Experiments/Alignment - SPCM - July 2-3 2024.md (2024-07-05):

July 2-3rd, 2024

SPCM updates

## **Alignment improvements**

- The linear polarizer (LP) is set to maximize power out of the PL202
- Both the LP and HWL mounts are checked for good fit, no tilting
- One iris moved to the end of the optical path before the beamsplitter (BS3) between the obj. and camera
- I can remove the BS3 and add cage rails to check the alignemnt further way
- I can remove the black plastic bellows between the top of the microscope body and the top of the objective to ensure that the beam is centered there
    - I ordered a alignment tool that will screw into the top of the objective so that I can check alignment there in the future more precisely

## **Beamsplitter compensation**

- I realized that the first beamsplitter (BS1) which attached the photodetector to the system applies a displacement to the beam whihc causes misalignment downstream
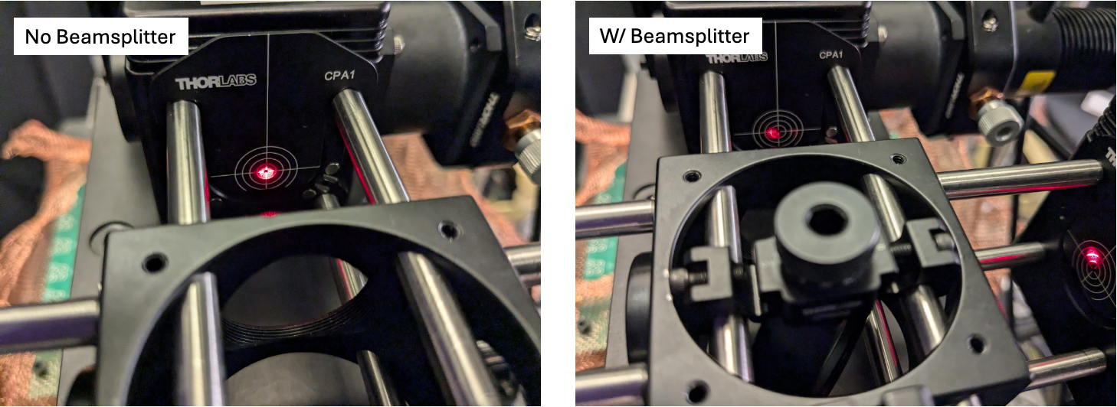
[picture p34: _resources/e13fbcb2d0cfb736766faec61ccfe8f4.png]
-  
- for this you can use a compensation plate such as the  
    [BCP4310](https://www.thorlabs.com/newgrouppage9.cfm?objectgroup_id=10662&pn=BCP4310)  *I ordered this.*  
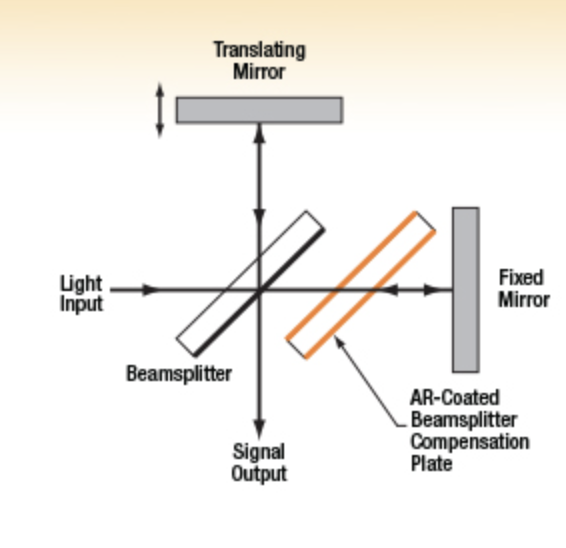
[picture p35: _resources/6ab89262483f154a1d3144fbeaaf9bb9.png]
    

## **Current optical path**


## **Quick reflection map test**
Now that the alingment is improved I want to see if I can get a reflectio map with a pretty large ND filter. Test is explained in image below. Used ND40A (aka 0.01% transmission)

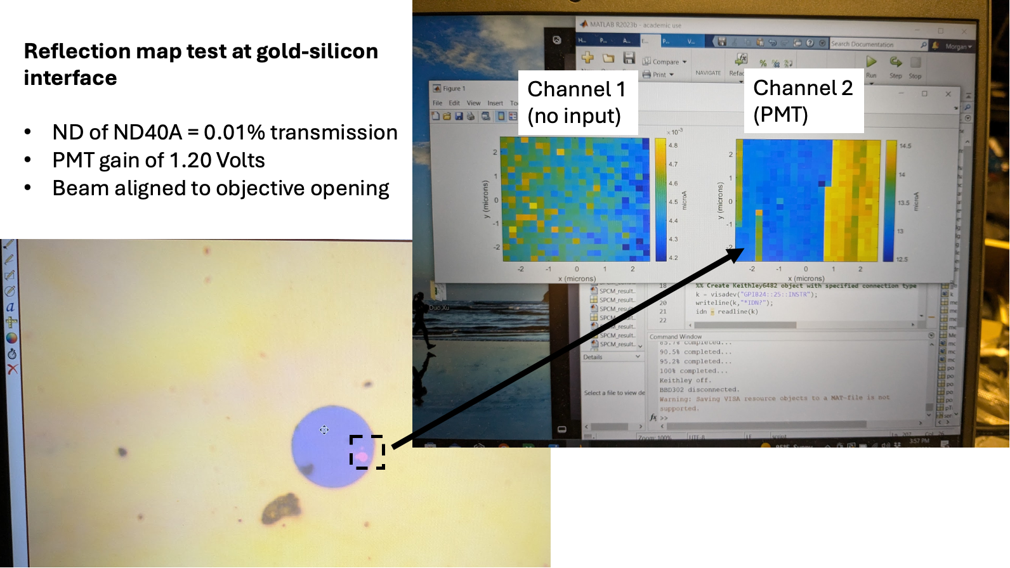
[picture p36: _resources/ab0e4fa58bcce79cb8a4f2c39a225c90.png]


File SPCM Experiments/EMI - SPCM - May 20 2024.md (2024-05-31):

# SPCM Laboratory Notebook May 20, 2024: PbTaSe2 measurement

## Setup
### Optical path:

```mermaid
graph LR
A[633 nm laser] -->B(ND filter)
    B --> C(1/2 W.P.)
    C --> D{B.S. 1}
    D --> E[PMT]
    D --> F{B.S. 2}
    G[Lamp] --> F
    F --> H{B.S. 3}
    H --> I(Camera)
    H --> J(Obj.)
    J --> K[Sample]
```

### Optical path components:

| Item              | Part # | About |
| :---------------- | :------: | ----: |
| 633 nm laser      | PL202	| Compact Laser Module with USB Connector, 635 nm, 0.9 mW (Typ.)  |
| ND filter, 0.01\% |   NE40A   | Neutral density filter |
| 1/2 Waveplate    | WPH05ME-633 | Linear polarizer, -- \% Reflection |
| Beamsplitter 1  | ...   | Splits optical path to PMT |
| PMT |  PMTSS   | Standard Sensitivity PMT Module|
| lamp  |  ...   | White lamp |
| Beamsplitter 2  |  ...   | Adds in white lamp |
| Beamsplitter 3  |  ...  | Splits between camera and objective |
| Camera tube    |  WFA4102   | Camera port 0.5x |
| Camera    |  8051C-USB   | 8 MP Color CCD Camera |
| Objective |  LMM40X-P01   | 40X Reflective Objective P01 Coating 0.50 NA BFL = Infinity |

BSW04 - Ø1/2" 50:50 UVFS Plate Beamsplitter, 400-700nm, t=3mm
BSW29P - 50:50 UCFS plate beamsplitter 600-1700nm
BSS10R - 25 x 36 mm 30:70 (R:T) UVFS Plate Beamsplitter, Coating: 400 - 700 nm, t = 1 mm
BSX10 - 90:10 (R:T) UVFS Plate Beamsplitter, Coating: 400-700 nm, t = 5 mm

## Sample

PbTaSe2 from 2DSemiconductor.com, deposited on HS39626-WO: SSP w/2 Semi-Std Flats & 2850 A°±5% Wet Thermal Oxide.

Electrodes fabricated around flakes in the MIT Nano lab May 23, 2023 by Morgan Blevins.

PPMS measurements performed on the "orange" flake by Thanh Ngyu





Starting with the "blue" flake on the PbTaSe2 chip 4, which is wirebonded to electrodes 4,5, 20, 21, and 22. First I do a quick reflection map of a flake that is not part of the circuit to confirm the system is working and confirm that there is no burning when no current is being measured.



Next I perform a reflection map of the entire flake now that I see the setup is working. 



## May 21, 2024



## May 23, 2024



## May 30, 2024
Last week I realized there was some stray signal coming from the X-Y MLS203 stage interferring with the current measurement from the board. This gave huge (hundreds of nanoAmps) currents that would spike out the measurement and make it uninterprittable. With some trial and error I found that (1) slowing the motors down to super low velocites and (2) raising the board several inches above the stage combined seem to get rid of this signal.

Using: 
velParams.Acceleration = 100;
velParams.MaxVelocity = 100;

Here is an updated picture of the setup (current two PCBs stacked since I have to soldier a new m.2 connector on the verion2 mainboards (version 1 was too small):


First ever attempt with the board suspended, I used the PbTaSe2_052323-4 chip. Actually looks like I'm getting a signal, but I'm going to now modify the code to measure reflection simultaneously. 



PbTaSe2_052323-4_SPCM_result_2024-05-30-2130

I don't intially recognize this shape, it does kind of appear to be the flake and electrode interface. I am now running a measurement over the same area but with no laser on to get a control. Uh oh, so I do see a sort of statified current measurement coming through in the same way. I just put my hand in between the board and stage and saw the signal dip. Gonna go get the EMI shielding from Thorlabs. 

The lines that aren't with the trend are when I tried to place the EMI shield/ put my hand in front:
NoLaser_SPCM_result_2024-05-30-1000

EMI sheilding from ThorLabs does not seem to help at all.My hand is more effective.

Reconfirmed that distance between board and stage is really helping -- signal goes WAY up when they are close, despite low velocity.

recall that i even picked up bad signals when measuring a resister as it was moved on the stage.

Motion vs. EMI. distance from stage makes it better-. EMI?



LaserOn_10inup_SPCM_result_2024-05-30-1000

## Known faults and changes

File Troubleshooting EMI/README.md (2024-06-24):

## Scanning Photocurrent Microscope Laboratory Notebook
### May 20, 2024: Possible electromagnetic inferference on PbTaSe2 photocurrent measurement
This lab notebook documents my setup and measurements for measuring spontaneous photocurrents in single crystal samples that are prepared in the nanofab. The principle and goal of this experiment is presented in the following papers:

1. [Ma, J., Gu, Q., Liu, Y. et al. Nonlinear photoresponse of type-II Weyl semimetals. Nat. Mater. 18, 476–481 (2019). https://doi.org/10.1038/s41563-019-0296-5]([url](https://doi.org/10.1038/s41563-019-0296-5))
2. [Jiang, J., Chen, Z., Hu, Y. et al. Flexo-photovoltaic effect in MoS2. Nat. Nanotechnol. 16, 894–901 (2021). https://doi.org/10.1038/s41565-021-00919-y]([url](https://doi.org/10.1038/s41565-021-00919-y))

### Experimental principle/examples

- Spatially local photoinduced current (local photocurrent) 
- Generated in a tight laser beam spot 
- Sensed far away at remote current-collecting–voltage-sensing contact
- Depending on laser power, the magnitude of current can be in the nanoAmp to microAmp range

<figure>
    Scanning photocurrent principle
</figure>

*Scanning photocurrent principle and the goal result of a SPCM measurement: a spatial map of photocurrent.*

 

### Optical path:



```mermaid
graph LR
A[633 nm laser] -->B(ND filter)
    B --> C(1/2 W.P.)
    C --> D{B.S. 1}
    D --> E[PMT]
    D --> F{B.S. 2}
    G[Lamp] --> F
    F --> H{B.S. 3}
    H --> I(Camera)
    H --> J(Obj.)
    J --> K[Sample]
```

### Optical components:

| Item              | Part # | About |
| :---------------- | :------: | ----: |
| 633 nm laser      | PL202	| Compact Laser Module with USB Connector, 635 nm, 0.9 mW (Typ.)  |
| ND filter, 0.01\% |   NE40A   | Neutral density filter |
| 1/2 Waveplate    | WPH05ME-633 | Linear polarizer, -- \% Reflection |
| Beamsplitter 1  | ...   | Splits optical path to PMT |
| PMT |  PMTSS   | Standard Sensitivity PMT Module|
| lamp  |  ...   | White lamp |
| Beamsplitter 2  |  ...   | Adds in white lamp |
| Beamsplitter 3  |  ...  | Splits between camera and objective |
| Camera tube    |  WFA4102   | Camera port 0.5x |
| Camera    |  8051C-USB   | 8 MP Color CCD Camera |
| Objective |  LMM40X-P01   | 40X Reflective Objective P01 Coating 0.50 NA BFL = Infinity |

## Sample

PbTaSe2 from 2DSemiconductor.com, deposited on HS39626-WO: SSP w/2 Semi-Std Flats & 2850 A°±5% Wet Thermal Oxide. Electrodes fabricated around flakes in the MIT Nano lab May 23, 2023 by Morgan Blevins.







Starting with the "blue" flake on the PbTaSe2 chip 4, which is wirebonded to electrodes 4,5, 20, 21, and 22. First I do a quick **reflection** map of the entire flake to confirm that the setup is working in reflection mode:



Mounted on the final PCB setup:



## Attempt to measure photocurrent: Electromagnetic Inference

Last week I realized there was some stray signal coming from the X-Y MLS203 stage interferring with the current measurement from the board. This gave huge (hundreds of nanoAmps) currents that would spike out the measurement and make it uninterprittable. With some trial and error I found that (1) slowing the motors down to super low velocites and (2) raising the board several inches above the stage combined seem to get rid of this signal.

Using: 
velParams.Acceleration = 100;
velParams.MaxVelocity = 100;

Here is an updated picture of the setup (current two PCBs stacked since I have to soldier a new m.2 connector on the verion2 mainboards (version 1 was too small):


First ever attempt with the board suspended, using the laser and illuminating the PbTaSe2_052323-4 chip. Actually looks like I'm getting a signal, but I'm going to now modify the code to measure reflection simultaneously. 



PbTaSe2_052323-4_SPCM_result_2024-05-30-2130

I don't intially recognize this shape, it does kind of appear to be the flake and electrode interface BUT I believe it is actually EMI. I will next run a measurement over the same area but with no laser on to get a control.

Current measurement when the flake is **NOT illuminated**. The expected map would just show constant noise, so it should just be a uniform color:

NoLaser_SPCM_result_2024-05-30-1000

Uh oh, so I see a sort of **statified current measurement** coming through in the same way, when I *should* just see noise/a uniform measurement. This is evidence than an EMI signal is coming from the MLS203. You see the same magnitude of EMI at the same y-position, creating a sort of field pattern perhaps. The x-poistion doesn't seem to have a pattern of EMI. I just put my hand in between the board and stage and saw the signal dip. Gonna go get the EMI shielding from Thorlabs. The lines in the plots above that aren't with the trend are when I tried to place the EMI shield/ put my hand in front.

Notes on trying to mitigate EMI:

- EMI sheilding from ThorLabs does not seem to help at all (at least the 1 layer I used). My hand is more effective.
- Distance from stage makes it better
- The PCB doesn't need to be touching the MLS203 for this interference to happen
- When MLS203 is OFF I see no interference. 
- Reconfirmed that distance between board and stage is really helping -- signal goes WAY up when they are close, despite low velocity.
- Recall that I even picked up bad signals when measuring a resister as it was moved on the stage, so it does not seem to be an issue with my PbTaSe2 sample.



LaserOn_10inup_SPCM_result_2024-05-30-1000

# June 21st, 2024
Testing the EMI with an Electromagnetic Field 

# June 24th, 2024
Built a Faraday cage to see if it gets rid of noise pattern.


Okay, so the Faraday cage did not actually fix the signal!! 

Now when I measure the signal when the XY stage is moving, I see that there is in fact a nonzero electromagnetic signal in the low frequency range. It appears to indeed be 10 Hz.

OK- it appears the issue was the RF interference with the wire, I placed the Electromagnetic Field tester in the setup while the map was running and saw a little jump in the masurement of RF everything the stage was at the peak in current signal along the path- do i knew that RF was getting into the cage somehow at that point. I then covered the holw SMA to BNC cable with the braided tinned copper that I ordered and WOW!!! The signal is finally gone. YAY. So the below meausmrent begins on the right side where the setup was sitting in the bent Mu-metal make shift cage and then at around +3 microns I pasued the measurement and moved it to the Faraday cage and BOOM barely ANY noise. This is AWESOME.







Round 2:

Round 3:


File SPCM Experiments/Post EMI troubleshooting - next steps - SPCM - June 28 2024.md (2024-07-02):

# SPCM Laboratory Notebook June 28, 2024:

## Setup
### Optical path:
I just added in linear polarizers before and after the HWP to determine polarization state:

```mermaid
graph LR
A[633 nm laser] -->BB(ND filter)
    BB --> B(Lin. Pol.)
    B --> C(H.W.P.)
    C --> CC(Lin. Pol.)
    CC --> D{B.S. 1}
    D --> E[PMT]
    D --> F{B.S. 2}
    G[Lamp] --> F
    F --> H{B.S. 3}
    H --> I(Camera)
    H --> J(Obj.)
    J --> K[Sample]
```

### Optical path components:

| Item              | Part # | About |
| :---------------- | :------: | ----: |
| 633 nm laser      | PL202	| Compact Laser Module with USB Connector, 635 nm, 0.9 mW (Typ.)  |
| ND filter, 0.01\% |   NE40A   | Neutral density filter |
| Lin. Polarizer    | LPVISE050-A | Linear polarizer, 38 \% unpol Transmission |
| 1/2 Waveplate    | WPH05ME-633 | Linear polarizer, -- \% Reflection |
| 1/2 Waveplate    | LPVISE050-A | Linear polarizer, 38 \% unpol Transmission |
| Beamsplitter 1  | ...   | Splits optical path to PMT |
| PMT |  PMTSS   | Standard Sensitivity PMT Module|
| Lamp  |  MWUVL1   | Neutral white LED |
| Beamsplitter 2  |  ...   | Adds in white lamp for imaging|
| Beamsplitter 3  |  ...  | Splits between camera and objective |
| Camera tube    |  WFA4102   | Camera port 0.5x |
| Camera    |  8051C-USB   | 8 MP Color CCD Camera |
| Objective |  LMM40X-P01   | 40X Reflective Objective P01 Coating 0.50 NA BFL = Infinity |

BSW04 - Ø1/2" 50:50 UVFS Plate Beamsplitter, 400-700nm, t=3mm
BSW29P - 50:50 UCFS plate beamsplitter 600-1700nm
BSS10R - 25 x 36 mm 30:70 (R:T) UVFS Plate Beamsplitter, Coating: 400 - 700 nm, t = 1 mm
BSX10 - 90:10 (R:T) UVFS Plate Beamsplitter, Coating: 400-700 nm, t = 5 mm

## State of the SPCM setup


I have a higher fidelity Faraday cage which I can screw into the SPCM MLS302 stage and importantly the SMA wire is also sheidled and attached the SMA on the PCB.
This has gotten rid of the EMI patterns and how I get ~30-40 nm noise that is mostly uniform across a spatial measurement.

Some to dos:

- edit Brady's board so that the mezzanines can be closer together (OR for now just mount the middle m2 connector and just use that)
- get better set screws for the mezzanine boards -- **ordered**
- prep the Bi2Te3 and TaIrTe4 samples -- in 5th floor of nano
- feel confident about polarization sweep
- talk to nanolab about why my basic fab keeps coming out really badly for the PPMS substrates

## Status of Samples

The PbTaSe2 from 2DSemiconductor.com, deposited on HS39626-WO: SSP w/2 Semi-Std Flats & 2850 A°±5% Wet Thermal Oxide. Electrodes fabricated around flakes in the MIT Nano lab May 23, 2023 by Morgan Blevins. PPMS measurements performed on the "orange" flake by Thanh Ngyu
This flake has falled off of the substrate. I don't know how it fell off but I think I needed to be more carefull of how I stored it between measurements, I think it was possibly blown off due to the AC in the lab or it was bumped and I didn't realize. 


# July 1st update



**UPDATES**
- Soldered on a new M.2 connector so I have a good mainboard PCB wb 
- Have a better screw connector to the mezzanine bpard
- Bi2Te3 and PbTaSe2 samples are wirebonded and ready to test, TaIrTe4 couldn't wirebond
- I made big improvements to alignment: had to better align the beam between the WFA2400 and the objective. Also need to have a lin. polarizer infront on the laser diode followed by the half-wave plate. And I now have an iris right in fron of the laser and then right before the WFA. I also removed the insert from the WFA2400 and added cage rails to test alignment way further out and this is what reallly improve the alignment down to the objective.
- Now the biggest issue is just the beam size of the PL202 as compared to the entry on the objective, I think I need to finally hook up the HeNe. Will need to decide how to attenuate the power (either get a [new laser](https://www.thorlabs.com/thorproduct.cfm?partnumber=HNLS008L#ad-image-0) or buy a [fiber attenuation kit](https://www.thorlabs.com/newgrouppage9.cfm?objectgroup_id=6162) ( about the same price...).
- If I turned it slowly, I got to the point when rotating the HWP did NOT seem to move the beam spot, which is a sign of alignment. 
- I think I can go forward with testing the Bi2Te3 sample tomorrow, I may not trust the coninuity of power as I sweep polarization but I can get a qualitative picture.
- The power meter is pretty annoying-- either the power of the PL202 is super jumpy or the meter is off. I'm gonna ask Mathias if he has a meter I could briefly borrow.

Current path:
```mermaid
graph LR
A[633 nm laser] -->AA(ND filter)
    AA --> BB(Iris)
    BB --> B(Lin. Pol.)
    B --> CC(H.W.P.)
    CC --> D{B.S. 1}
    D --> E[PMT]
    D --> DD(Iris)
    DD --> F{B.S. 2}
    G[Lamp] --> F
    F --> H{B.S. 3}
    H --> I(Camera)
    H --> J(Obj.)
    J --> K[Sample]
```

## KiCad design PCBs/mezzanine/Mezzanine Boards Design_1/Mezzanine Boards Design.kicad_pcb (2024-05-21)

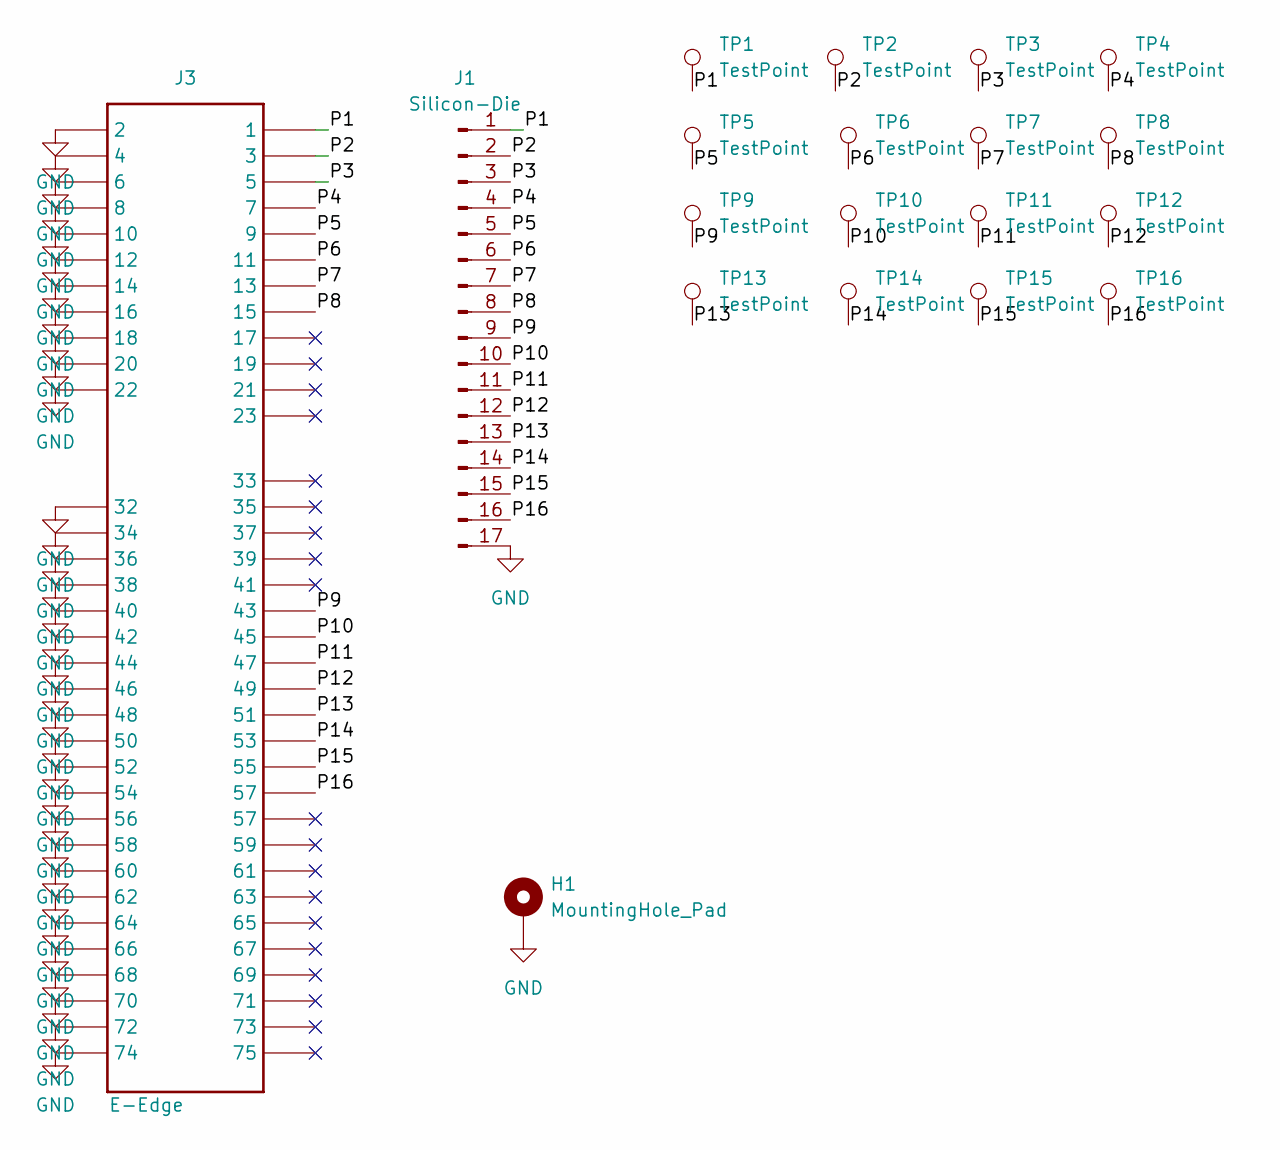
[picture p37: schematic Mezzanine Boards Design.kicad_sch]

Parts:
H1: MountingHole_Pad; MH_2mm
J1: Silicon-Die; new_sillicon_die_footprint
J3: E-Edge; E-Key_Edge
TP1, TP2, TP3, TP4, TP5, TP6, TP7, TP8, TP9, TP10, TP11, TP12, TP13, TP14, TP15, TP16: TestPoint; TestPoint_Pad_1.5x1.5mm

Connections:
/P1: J1.1, J3.1, TP1.1
/P2: J1.2, J3.3, TP2.1
/P3: J1.3, J3.5, TP3.1
/P4: J1.4, J3.7, TP4.1
/P5: J1.5, J3.9, TP5.1
/P6: J1.6, J3.11, TP6.1
/P7: J1.7, J3.13, TP7.1
/P8: J1.8, J3.15, TP8.1
/P9: J1.9, J3.43, TP9.1
/P10: J1.10, J3.45, TP10.1
/P11: J1.11, J3.47, TP11.1
/P12: J1.12, J3.49, TP12.1
/P13: J1.13, J3.51, TP13.1
/P14: J1.14, J3.53, TP14.1
/P15: J1.15, J3.55, TP15.1
/P16: J1.16, J3.57, TP16.1
GND: H1.1, J1.17, J3.2, J3.4, J3.6, J3.8, J3.10, J3.12, J3.14, J3.16, J3.18, J3.20, J3.22, J3.32, J3.34, J3.36, J3.38, J3.40, J3.42, J3.44, J3.46, J3.48, J3.50, J3.52, J3.54, J3.56, J3.58, J3.60, J3.62, J3.64, J3.66, J3.68, J3.70, J3.72, J3.74

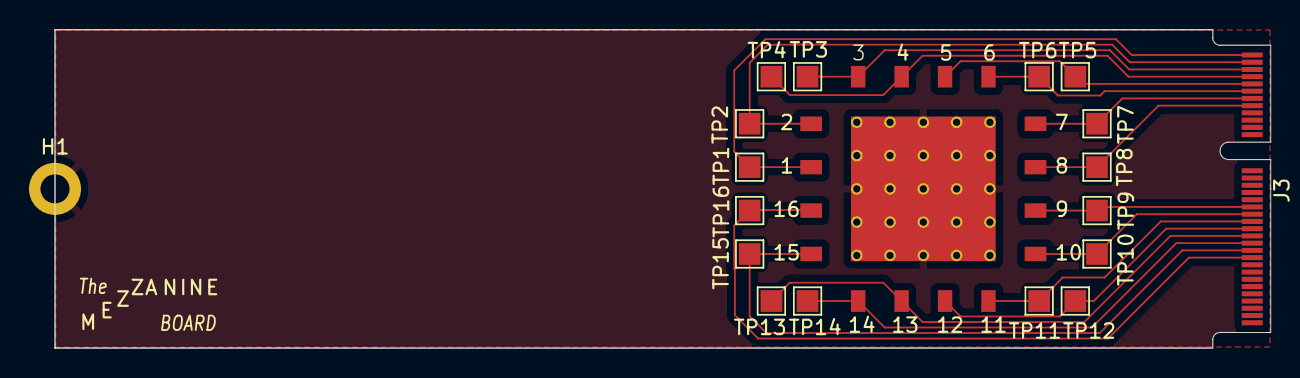
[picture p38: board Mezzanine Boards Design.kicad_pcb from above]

Board: 2 copper layers, 84.0 x 22.0 mm, 19 parts (0 on the bottom side), 17 nets.

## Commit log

2024-05-20 Rename PCBs/Gerber_PCB_UROP Project_2.zip to PCBs/mainboard/Gerber_PCB_UROP Project_2.zip
2024-05-20 Update and rename PCBs/PCB_UROP Project_2_2024-05-20.pcbdoc to PCBs/mainboard/PCB_UROP Project_2_2024-05-20.pcbdoc
    [PCB_UROP Project_2_2024-05-20.pcbdoc]
2024-05-20 Update and rename PCBs/Schematic_UROP Project_2024-05-20.svg to PCBs/mainboard/Schematic_UROP Project_2024-05-20.svg
2024-06-11 Add files via upload
    This is the code I used to control the MLS203 and the Keithley 6482 to make current measurements.
2024-06-11 Add files via upload
    Documentation of Mezzanine board and electrode design code
2024-07-02 June-July: Post EMI troubleshooting- sample and alignment.md
